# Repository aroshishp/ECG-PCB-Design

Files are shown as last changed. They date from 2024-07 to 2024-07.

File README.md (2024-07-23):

This repository contains the project files for designing a PCB of an Electrocardiogram in KiCad.

Images are attached below.

<p align='center'>
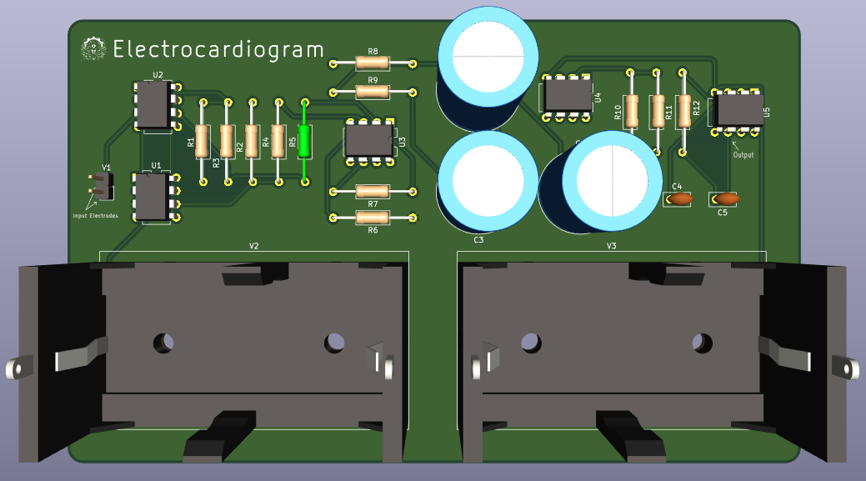
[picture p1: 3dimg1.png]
  
  <br><br>
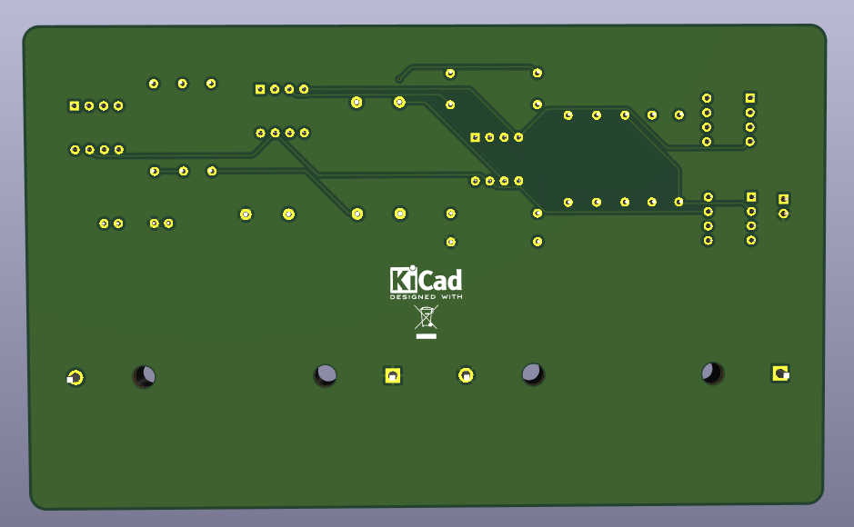
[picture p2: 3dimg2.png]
  
</p>

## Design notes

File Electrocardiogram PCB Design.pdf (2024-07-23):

## ELECTROCARDIOGRAM PCB DESIGN

PROJECT REPORT

This project aims to demonstrate the functioning and principles of an electrocardiogram and design its PCB using KiCad.

An electrocardiogram (ECG) is a medical test to check the functioning of the heart. The beats of the heart generate electrical impulses which are detected by electrodes connected to a person’s arms and legs. These pulses are then visualized on a computer to help doctors diagnose any underlying diseases or malfunctions of the heart.

The characteristics, design and working of the system is explained below.

a) Desired Characteristics and Functionalities
Differential Amplifier – It should amplify the small electrical impulses from the heart so that they can be processed without getting attenuated in the process.
Notch Filter – The electrical wiring of a building carries AC power at 50 Hz which produces significant noise in the readings. To specifically filter this out, a band-stop filter has to be used.
Low Pass Filter – Other interferences from various sources have to be filtered out and signals relevant to the reading should be retained. As relevant readings have low frequencies, a low-pass filter must be used.
b) Schematic Diagram
The three components of the circuit as described above were drawn and cascaded as shown below:
Differential Amplifier
3 electrodes are attached to the patient’s body. Op-Amps U1 and U2 are the input buffers and U3 amplifies the signal. All three are LM741 Operational Amplifier ICs. PIN 3 of U1 and U2 receive two electrode inputs from the patient. The third electrode is connected to ground. The outputs of U1 and U2 are passed to U3 which amplifies the inputs. For the purpose of drawing this schematic in KiCad, the PIN 3 of U1 was grounded and PIN 3 of U2 was provided an offset of 1mV to simulate the small difference in the input signals. Note that the red wires are connected to +15V and black wires are connected to -15V.

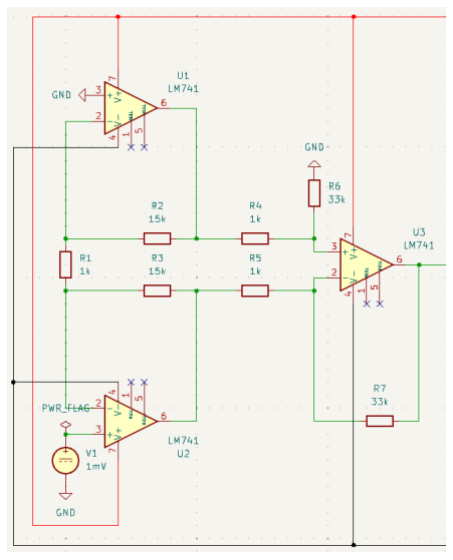
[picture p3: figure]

Notch Filter

This is the schematic of the Notch Filter. The input is taken from PIN 6 (output pin) of U3 in the differential amplifier. The notch filter is designed to filter out electrical grid noise of 50 Hz frequency and amplify the remaining signals. The output contains the filtered signals and is passed to the low-pass filter.

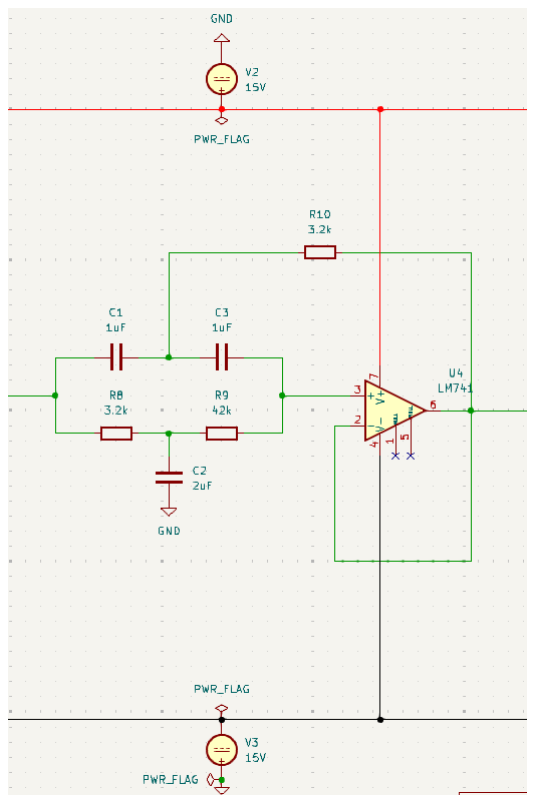
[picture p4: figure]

Low-Pass Filter

The low-pass filter takes the filtered signal from the Notch filter and further removes high frequency noise from the signal. It is a second-order active low-pass filter that uses the LM741 IC as its op-amp. The output signal is through PIN 6 (output pin) of the IC.

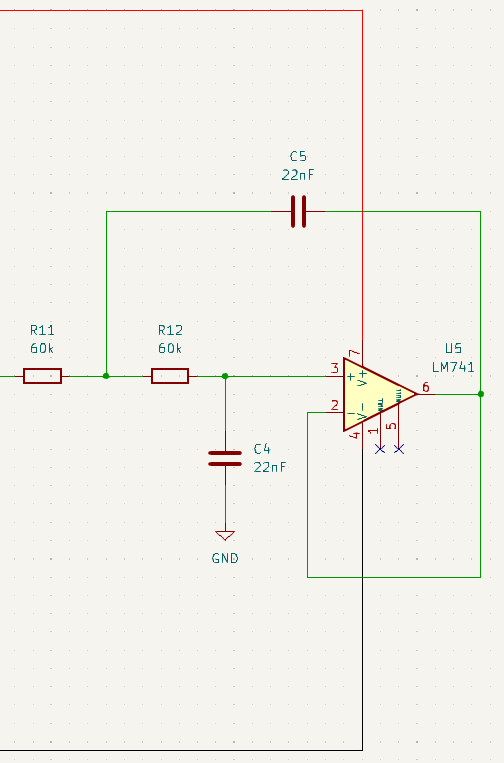
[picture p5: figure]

The complete circuit is provided below.

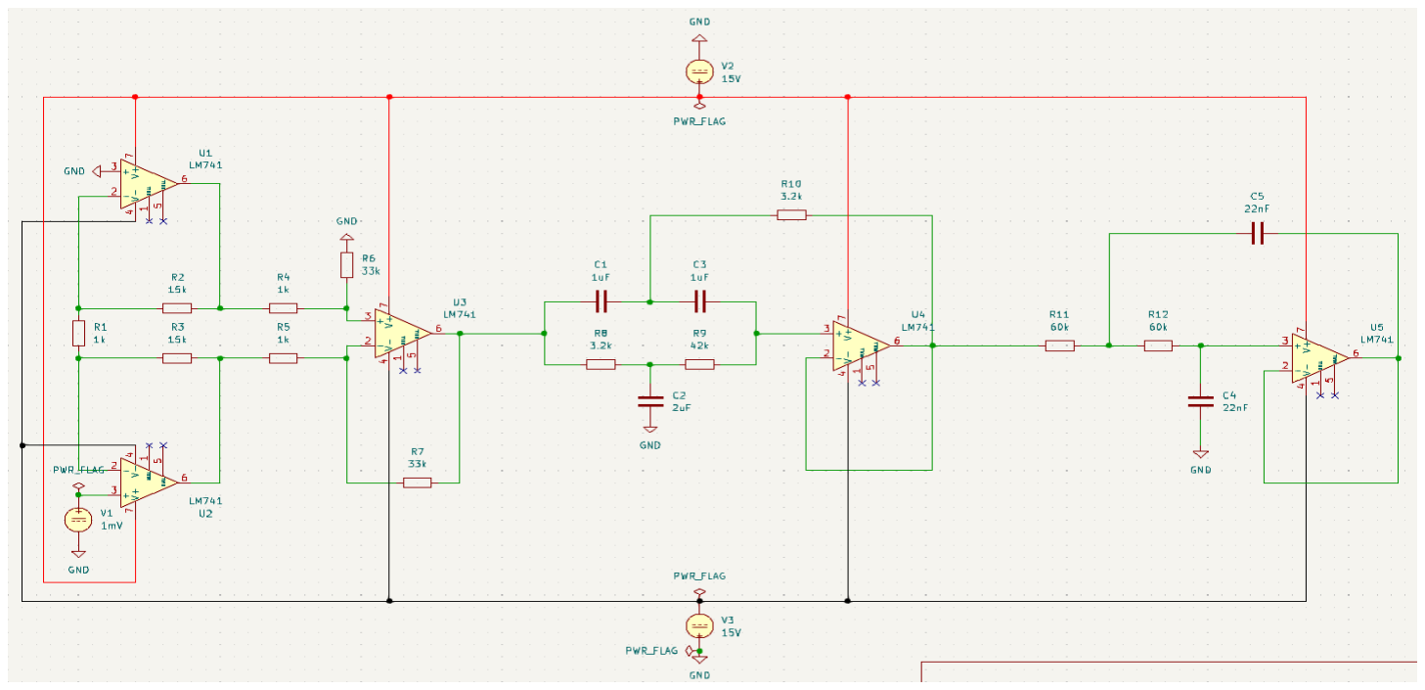
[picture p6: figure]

c) Working of the System
Differential Amplifier
The ECG gets its input through electrodes attached to the body, which are small electrical impulses. These are amplified by a differential amplifier that amplifies these signals. The differential amplifier comprises of 3 operational amplifiers (LM741) two of which take in the inputs from the electrodes and act as input buffers (have a gain of 1 but increase the power of the signals). The third op-amp is the differential amplifier which amplifies the signals due to the small difference between them and rejects any common signals.

Notch Filter
A Notch Filter is a band-stop filter, a filter that allows frequencies outside a certain range to pass. It is created using twin T configuration (involves 2 ‘T’s built using resistors and capacitors). Here, it is required to filter out the 50 Hz frequency, which acts as noise (or a “hum”) in the signal. This noise is generated because the electrical grid of the room where the readings are being taken carries AC current at 50 Hz frequency, which causes significant effects in the readings, which are also of low frequencies. The output signal is again amplified by another op-amp with a resistor.

Low-Pass Filter
The third stage contains a low pass filter. A low-pass filter is a filter that allows frequencies below a certain value to pass and attenuates higher frequencies. The type of low-pass filter used here is a second order active low-pass filter that uses an op-amp. Our heart beats at around 72 beats per minute which is 1.2 Hz. However, the ECG signal is composed of several waveforms:
1. P-Wave: Represents atrial depolarization, has low frequency (5 – 30 Hz)
2. QRS Complex: Represents ventricular depolarization, has comparatively higher frequency (up to or sometimes greater than 100 Hz)
3. T-Wave: Represents ventricular repolarization (0 – 10 Hz)

As a result, we cannot directly apply a low pass filter of cutoff around 1.2 Hz since we need to let the other essential signals pass through. Therefore, a low pass filter of around 120 Hz is created to allow for abnormalities.

Frequencies higher than this are most likely noise, such as electromagnetic interference by radios or muscle noise and can be filtered out.

d) Power Rating
To estimate the power consumption of the circuit, we need to consider the powerconsumption of the operational amplifiers used. The datasheet of LM741 mentions that in our operating conditions (Vs = ±15V, Temp 25C), the power consumption is typically 50mW and maximum is 85mW.

Therefore, since there are 5 op-amps, the average power consumption would be around 0.25 W, with maximum of 0.425 W.
The power consumption of the resistors would be negligible because of the current flowing would be very small in this application of measuring heart rates. Even after amplification, the current would not be significant enough to affect power consumption.

Capacitors do not consume power, they either store it (for DC inputs) or have charge and discharge cycles (for AC inputs). In our case the DC inputs are only provided to the op-amps for amplification, so we can consider the pulses to be a form of AC.

The thicknesses of the wire during PCB design were decided by considering the power consumption to be 0.5W, which provides a sufficient buffer for unprecedented fluctuations.

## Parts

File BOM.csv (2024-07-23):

Id | Designator | Footprint | Quantity | Designation | Supplier and ref
1 | C3,C1 | C_Radial_D16.0mm_H31.5mm_P7.50mm | 2 | 1uF
2 | R2,R3 | R_Axial_DIN0207_L6.3mm_D2.5mm_P15.24mm_Horizontal | 2 | 15k
3 | R9 | R_Axial_DIN0207_L6.3mm_D2.5mm_P15.24mm_Horizontal | 1 | 42k
4 | C2 | C_Radial_D16.0mm_H31.5mm_P7.50mm | 1 | 2uF
5 | V3,V2 | BatteryHolder_Bulgin_BX0036_1xC | 2 | 15V
6 | R8,R10 | R_Axial_DIN0207_L6.3mm_D2.5mm_P15.24mm_Horizontal | 2 | 165
7 | U1,U5,U4,U2,U3 | DIP-8_W7.62mm | 5 | LM741
8 | R11,R12 | R_Axial_DIN0207_L6.3mm_D2.5mm_P15.24mm_Horizontal | 2 | 60k
9 | C4,C5 | C_Disc_D5.0mm_W2.5mm_P2.50mm | 2 | 22nF
10 | R6,R7 | R_Axial_DIN0207_L6.3mm_D2.5mm_P15.24mm_Horizontal | 2 | 33k
11 | V1 | PinHeader_1x02_P2.54mm_Vertical | 1 | 1mV
12 | R1,R4,R5 | R_Axial_DIN0207_L6.3mm_D2.5mm_P15.24mm_Horizontal | 3 | 1k

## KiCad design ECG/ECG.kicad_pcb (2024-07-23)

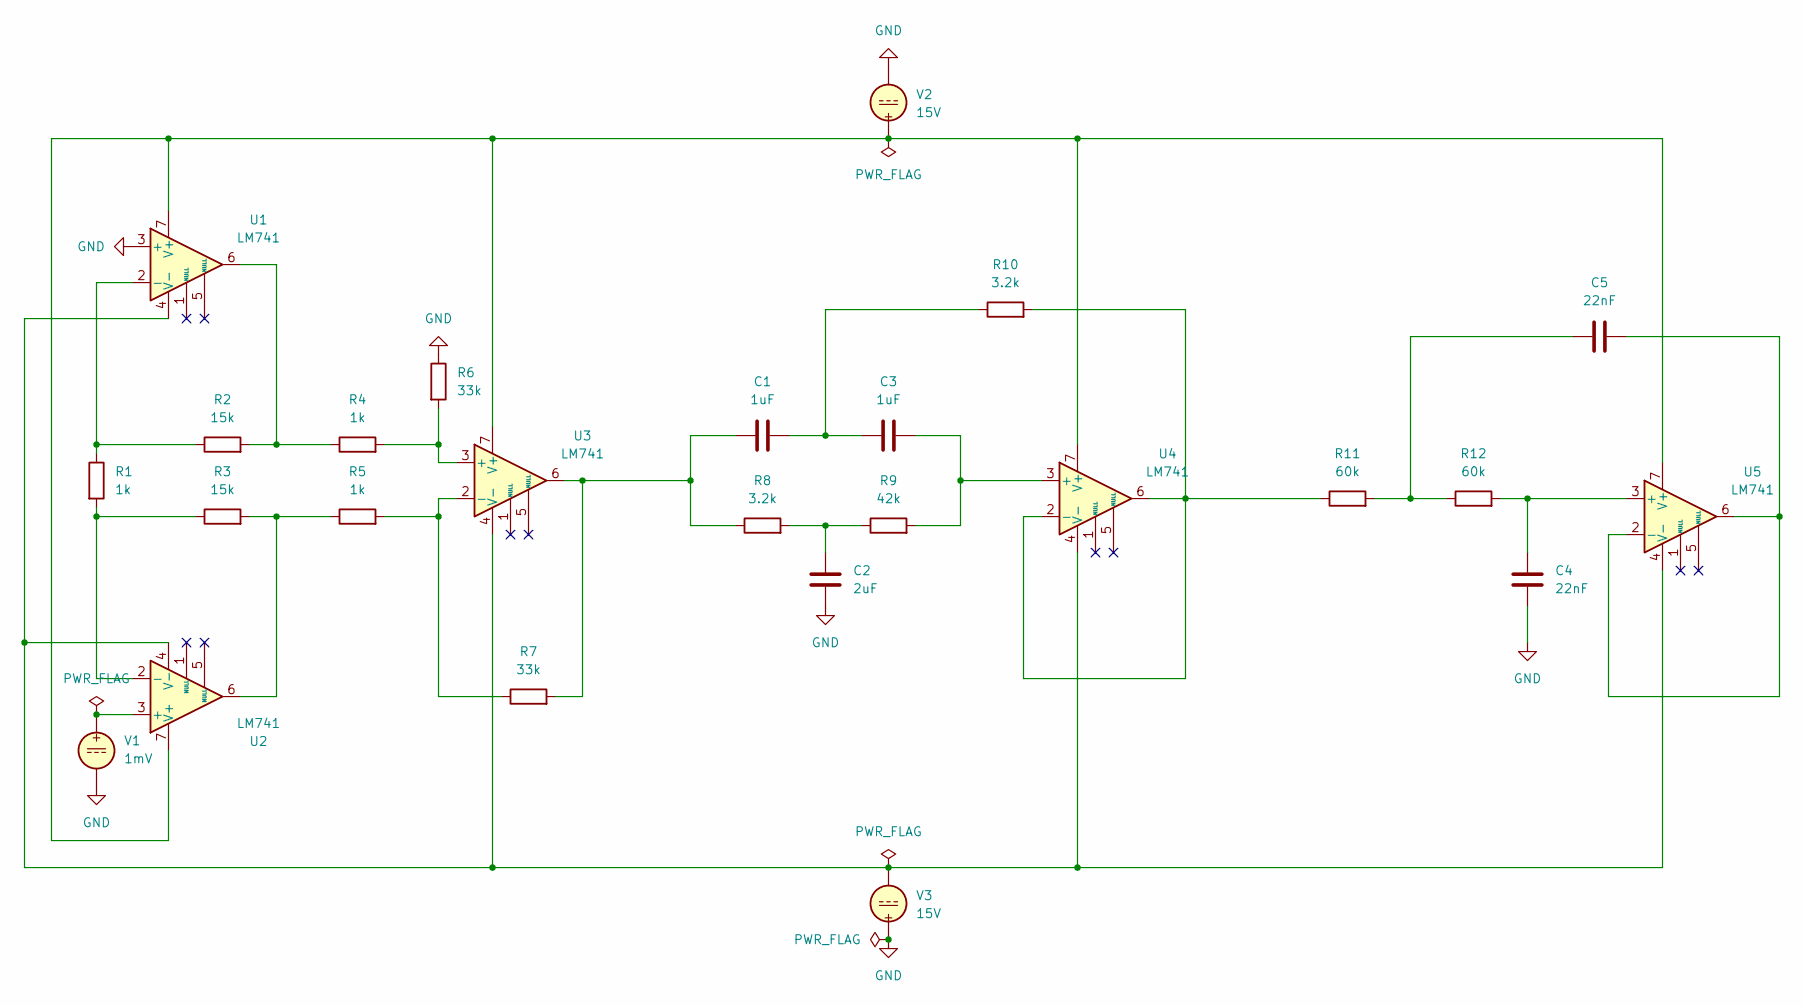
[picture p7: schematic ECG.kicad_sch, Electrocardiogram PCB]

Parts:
C1, C3: 1uF; C_Radial_D16.0mm_H31.5mm_P7.50mm
C2: 2uF; C_Radial_D16.0mm_H31.5mm_P7.50mm
C4, C5: 22nF; C_Disc_D5.0mm_W2.5mm_P2.50mm
R1, R4, R5: 1k; R_Axial_DIN0207_L6.3mm_D2.5mm_P15.24mm_Horizontal
R2, R3: 15k; R_Axial_DIN0207_L6.3mm_D2.5mm_P15.24mm_Horizontal
R6, R7: 33k; R_Axial_DIN0207_L6.3mm_D2.5mm_P15.24mm_Horizontal
R8, R10: 3.2k; R_Axial_DIN0207_L6.3mm_D2.5mm_P15.24mm_Horizontal
R9: 42k; R_Axial_DIN0207_L6.3mm_D2.5mm_P15.24mm_Horizontal
R11, R12: 60k; R_Axial_DIN0207_L6.3mm_D2.5mm_P15.24mm_Horizontal
U1, U2, U3, U4, U5: LM741; DIP-8_W7.62mm
V1: 1mV; PinHeader_1x02_P2.54mm_Vertical
V2, V3: 15V; BatteryHolder_Bulgin_BX0036_1xC

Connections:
GND: C2.2, C4.2, R6.1, U1.3 (+), V1.2, V2.2, V3.1
unnamed: C1.1, R7.2, R8.1, U3.6
unnamed: C1.2, C3.1, R10.1
unnamed: C2.1, R8.2, R9.1
unnamed: C5.2, R11.2, R12.1
unnamed: R2.2, R4.1, U1.6
unnamed: R3.2, R5.1, U2.6
unnamed: R1.1, R2.1, U1.2 (-)
unnamed: U1.7 (V+), U2.7 (V+), U3.7 (V+), U4.7 (V+), U5.7 (V+), V2.1
unnamed: U1.4 (V-), U2.4 (V-), U3.4 (V-), U4.4 (V-), U5.4 (V-), V3.2
unnamed: U2.3 (+), V1.1
unnamed: R1.2, R3.1, U2.2 (-)
unnamed: R4.2, R6.2, U3.3 (+)
unnamed: R5.2, R7.1, U3.2 (-)
unnamed: C3.2, R9.2, U4.3 (+)
unnamed: R10.2, R11.1, U4.2 (-), U4.6
unnamed: C4.1, R12.2, U5.3 (+)
unnamed: C5.1, U5.2 (-), U5.6

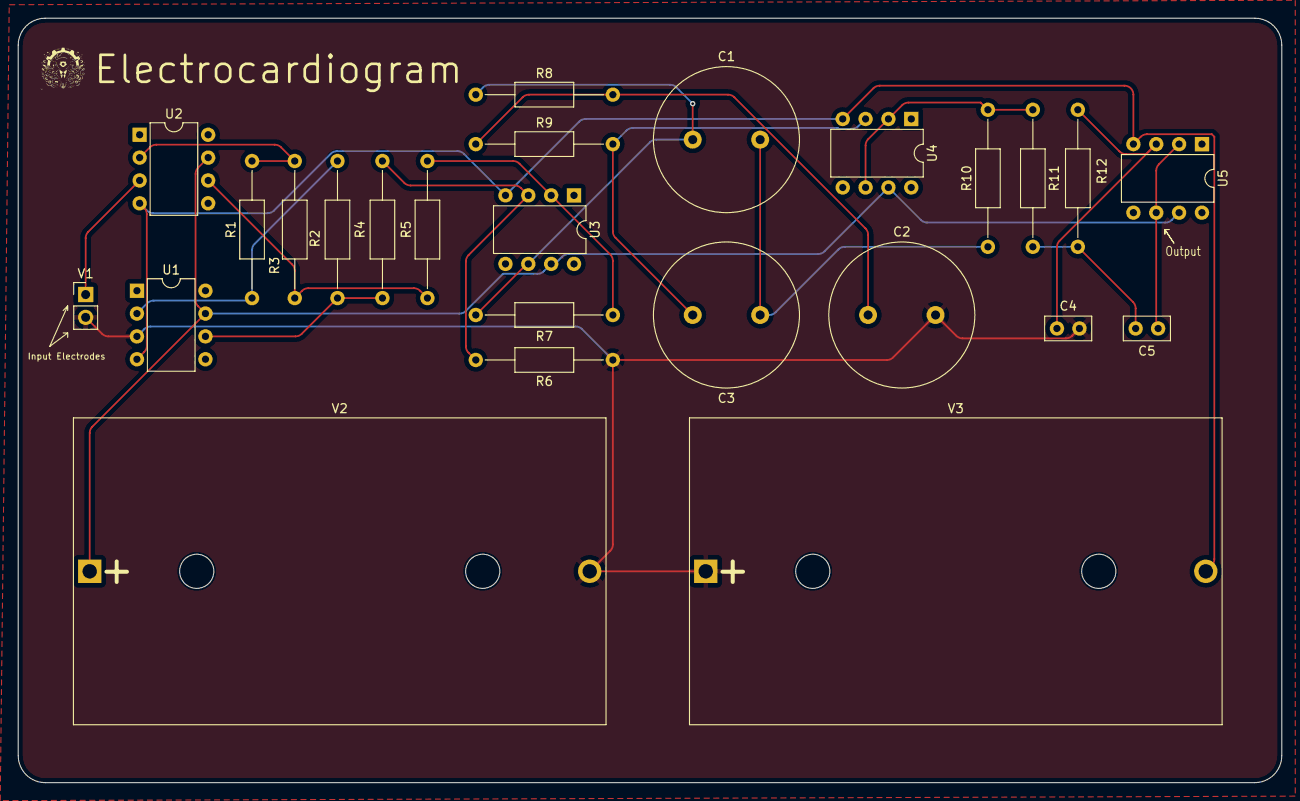
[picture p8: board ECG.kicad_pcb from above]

Board: 2 copper layers, 140.5 x 85.0 mm, 25 parts (0 on the bottom side), 18 nets.
